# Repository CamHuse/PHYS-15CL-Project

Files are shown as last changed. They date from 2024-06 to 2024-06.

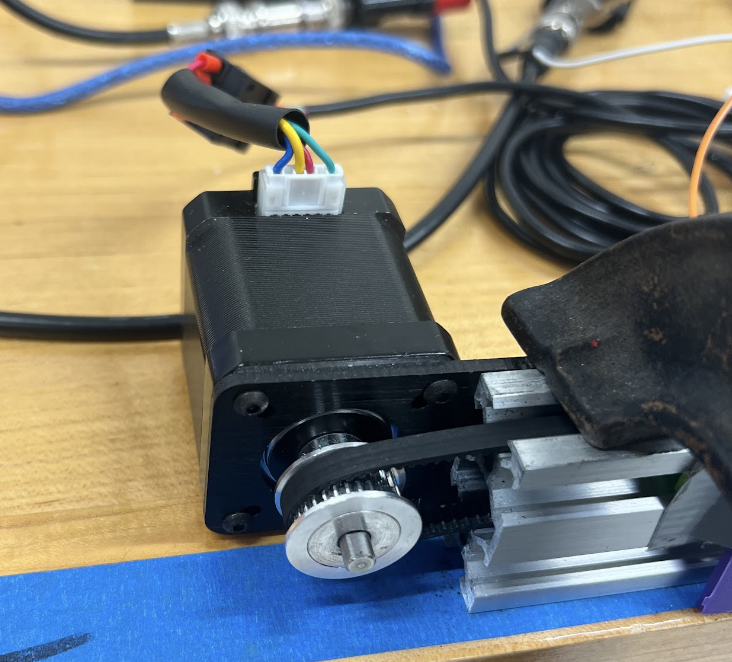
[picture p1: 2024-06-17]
.assets/StepperMotor.png

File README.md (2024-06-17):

# Inverted Pendulum

This GitHub repository documents the project completed by Eliott Schaffer, Jeremy Lauro, and Cameron Huse for PHYS 15C at UCSB during the Spring Quarter of 2024.

Each folder contains different aspects of the project, including significant files and specific documentation.

[Link to Presentation with Photos and Video Demonstrations](https://docs.google.com/presentation/d/1EEgrXbiuC8zDKRkNd1JOHVO5JtM1_9yI2Myhj0fMQJY/edit?usp=sharing)

## Schematic

A full quality version is also [avaliabe](https://github.com/CamHuse/PHYS-15CL-Project/blob/d5d5c650847254214024270f439a0aa117e3549a/Control%20Code/IntervedPendulum_SCH.pdf)

## Assembly Instructions:

1. Order the necessary parts.
2. Print the final version of the 3D models.
3. Construct the base rail system.
4. Attach the 3D printed parts to the moving cart and install the endstop switches.
5. Attach the encoder, ball bearings, and pendulum rod to the cart.
6. Wire the encoder and endstop switches to the Arduino as described in the schematic.
7. Wire the stepper motor controller to the Arduino as described in the schematic.
8. Wire the 24V DC supply to the stepper motor controller and connect the 4 stepper wires.
9. Run the Arduino Mega.

## Components

Inverted Pendulum System

### Cart

The cart consists of a base plate that holds the wheels connected to the rail and two 3D-printed pieces that serve as the base for the pendulum. It moves along a rail and supports the encoder and pendulum. The cart's design ensures precise movement and stability during operation.

### Pendulum

The pendulum is mounted on the cart and connected to the rotary shaft via a T-bracket. It swings freely, and its horizontal shaft is connected to the encoder, allowing us to read the pendulum's position at any moment in time.

### Encoder

The encoder, situated on the cart, measures the pendulum's angular position and velocity. It communicates with the Arduino via SPI (Serial Peripheral Interface), providing real-time positional data for system control and analysis.

System Close-Up

### Limit Switches

Limit switches are installed to detect the center of the rail and prevent the cart from exceeding the rail boundaries. These switches are electrically connected to the Arduino via interpret pins, allowing us to immediately stop the motor if the cart drifts too far either way.

Assembled System

### Stepper Motor

The stepper motor drives the cart along the rail. We control the motor by continuously sending a PWM signal to specify its desired speed. It is connected to the cart through a pulley system and powered by a 24V DC supply, with control signals provided by the Arduino.



---

## Swing-Up Phase
The swing-up logic aims to align the pendulum upright relative to its zero point, directly downward. When the pendulum is to the right of the zero point (positive angle), the system directs the cart right, applying torque to increase the pendulum's kinetic energy. Conversely, when the pendulum is to the left of the zero point (negative angle), the system directs the cart left. This repeated motion helps the pendulum swing back and forth, gradually reaching a vertical position while keeping the cart within the rail's limits. Below is a plot of the pendulum's angle overtime during the swing-up phase.



--
## Control System



### Sensors

The sensors used in this control system are responsible for gathering input data from the environment. They provide crucial information that the controller utilizes to make decisions and adjustments. The sensors included are:

- Absolute Encoder
- End-Stop Switches
- Computer Interface

### Controller

The controller processes the data received from the sensors and determines the appropriate actions to achieve the desired system behavior or state. This project utilized a PID controller. For a detailed explanation, see the control code folder in our repository.

### Actuators

Actuators are devices the system's controller controls to guide the system into the desired state. The only actuator utilized in this system is the stepper motor.

## Notes For Future Builders

Instead of getting a Nema17 Stepper motor kit, opt for a Nema23 kit. We were having over-torquing problems. 

Steel rotary shafts are hard to use and get a ball bearing on, and it is much easier to add threads to an aluminum rod and file it. 

Going with a DC motor design is more conventional and will allow for more direct torque control compared to a stepper motor.

If going for a stepper motor design, MATLAB and Raspberry Pis are too slow to count the steps of the stepper motor, a different design philosophy or extra distance sensor must be used.

--

Feel free to explore the repository and refer to the provided documentation for more details on each part of the project.

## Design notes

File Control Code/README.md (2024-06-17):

## Files

- `PIDPendulumControl.ino`: Implementation of PID control for the inverted pendulum.
- `README.md`: Documentation file.
  
## PID Control

Proportional-Integral-Derivative (PID) control is a feedback mechanism widely used in control systems. It calculates an error value as the difference between a desired setpoint and a measured variable. In our case, the measured variable is the angle of the pendulum provided by the absolute encoder, and the desired setpoint is 180 degrees from vertically down. The controller attempts to minimize the error by adjusting the process using three terms: proportional $(K_p)$, integral $(K_i)$, and derivative $(K_d)$.

### PID Control Implementation 

The control output $u(t)$, used to control the speed of the stepper motor, is given by:

$$ u(t) = K_p e(t) + K_i \int e(t)  dt + K_d \frac{d e(t)}{d t} $$

Where:
- $e(t)$ is the error at time $t$.
- $K_p$ is the proportional gain.
- $K_i$ is the integral gain.
- $K_d$ is the derivative gain.
  
Note: The parameters $\( K_p \)$, $\( K_i \)$, and $\( K_d \)$ defined in `PIDPendulumControl.ino` are specific to our cart-pendulum system with a pendulum mass and weight particular to our system, so they may not be directly applicable to other systems without retuning. Adjust these parameters based on your specific system's dynamics to achieve optimal control performance.

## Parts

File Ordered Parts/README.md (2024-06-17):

# Inverted Pendulum Ordered Parts

This repository contains 3D models for components used in our inverted pendulum project.

### Components:

- **Threaded Rotary Shaft:** Primary rotary shaft integrated into the Hub, featuring threads for connection to the T-Bracket.

- **CUI_Device:** Encoder used to measure the angle of the inverted pendulum.

- **Hub Pad:** Main cart connecting to the rail and pulley system, with the hub attaching for movement.

- **MS085 (Limit Switch):** Used to detect the ends of the rail and prevent the cart from running off.

- **V-Slot Belt Driven Actuator:** Model of the rail system without attached inverted pendulum components.

### Parts List
For an exhaustive list of the parts used in this project, please refer to the [Parts List](https://docs.google.com/spreadsheets/d/1zZ4MJvw8T9NZ0qEtBUQf3BjHz44bl6Pn-mwk28OsQ0s/edit?usp=sharing).

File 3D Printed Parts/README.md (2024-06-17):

This folder contains all the 3D models for parts used to assemble the inverted pendulum. The parts are as follows:

- **Ball Bearing Holder**: Secures the ball bearing in place on the Hub.
- **Bracket Rail Connector**: Attaches the Switch Bracket to the rail.
- **Hub**: Houses the encoder, rotary shaft, and ball bearings needed for the inverted pendulum. The Hub connects to the cart, allowing the entire inverted pendulum system to move.
- **Spacer**: A spacer was needed to correctly assemble the pulley system, as the one that was ordered was too small.
- **Switch Bracket**: Houses the limit switches and connects them to the rail.
- **T-Bracket**: Connects the rotary shaft to the main inverted pendulum rod.

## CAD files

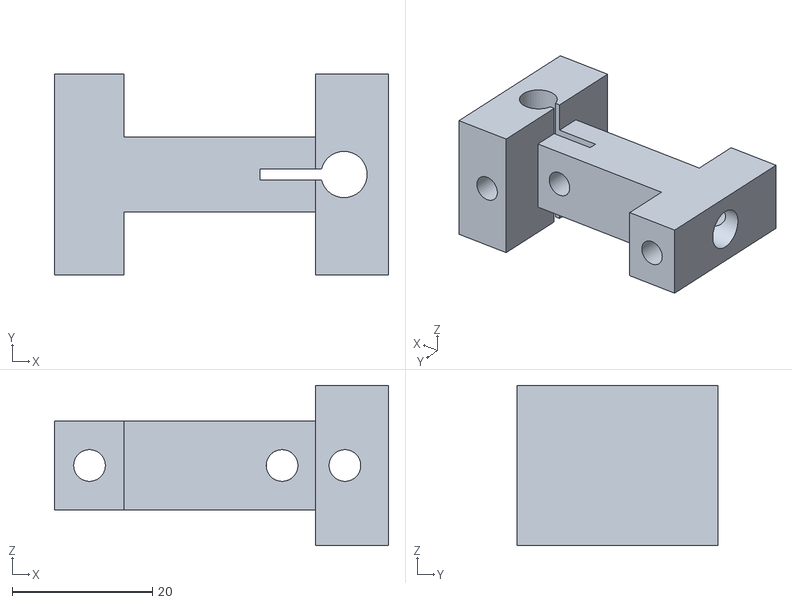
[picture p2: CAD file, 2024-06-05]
3D Printed Parts/T-Bracket Version 2 v19.stl
47.7 x 28.7 x 22.9

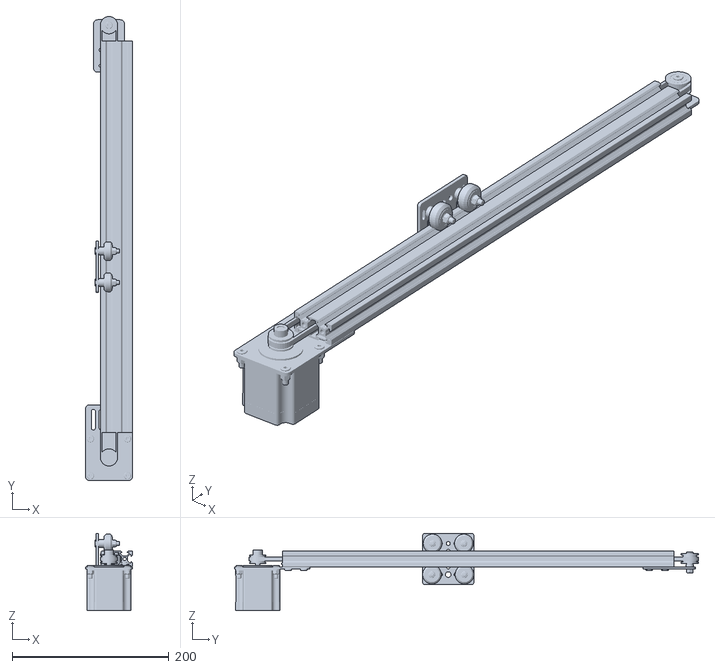
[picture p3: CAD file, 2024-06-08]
Ordered Parts/Nema 23 V-Slot Belt Driven Actuator v3.stl
60.0 x 592.6 x 98.6

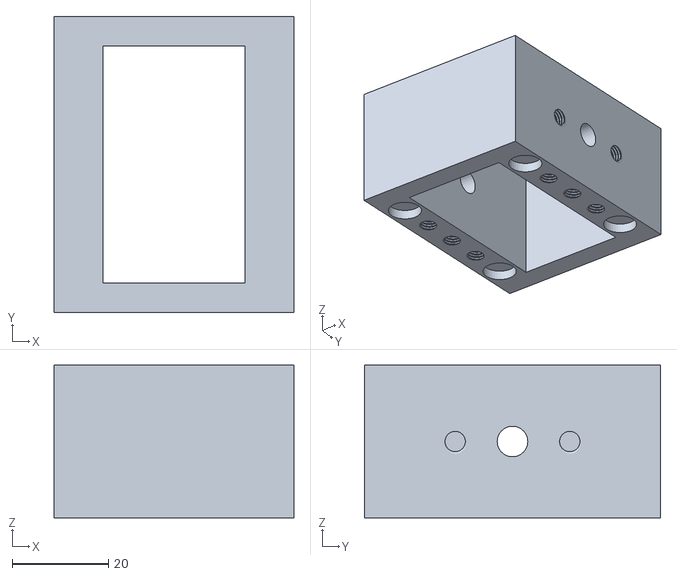
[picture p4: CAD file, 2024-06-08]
Prototype 3D Prints/Hub Design v7.stl
49.9 x 61.5 x 31.8

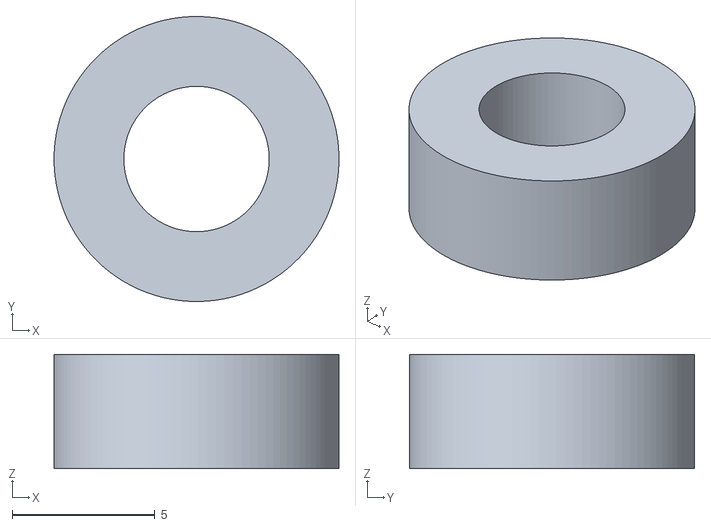
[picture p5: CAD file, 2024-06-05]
3D Printed Parts/Spacer v2.stl
10.00 x 10.00 x 4.00

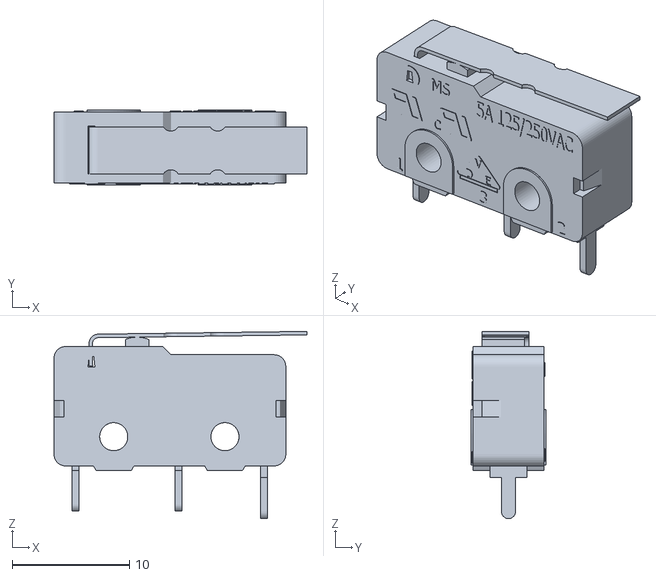
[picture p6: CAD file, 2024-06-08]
Ordered Parts/MS085xx02FxxxP1A v2.stl
21.6 x 6.40 x 16.0

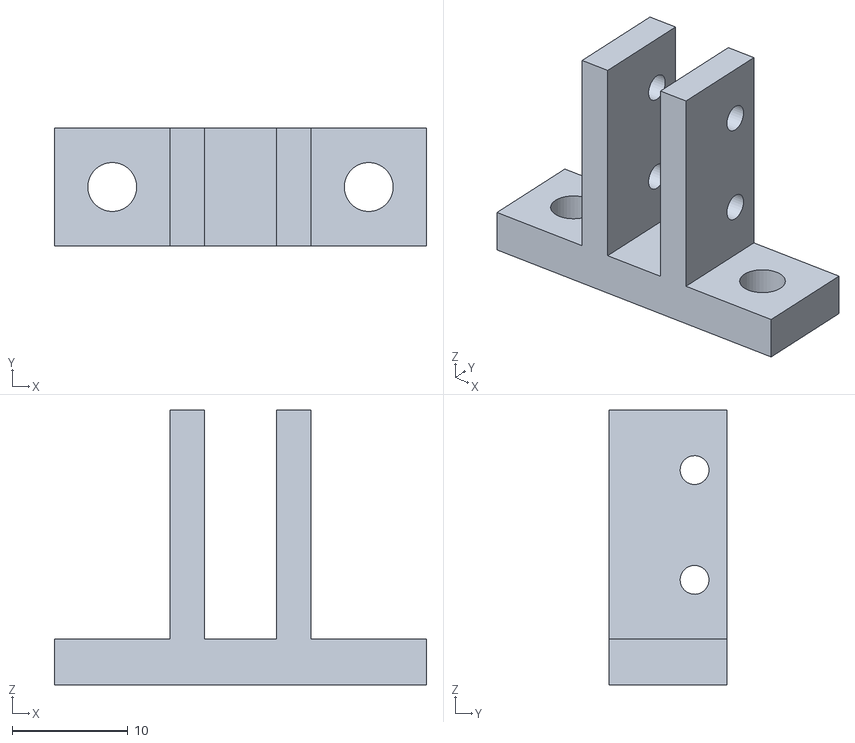
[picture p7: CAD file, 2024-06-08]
Prototype 3D Prints/Switch Bracket v3.stl
32.2 x 10.2 x 23.8

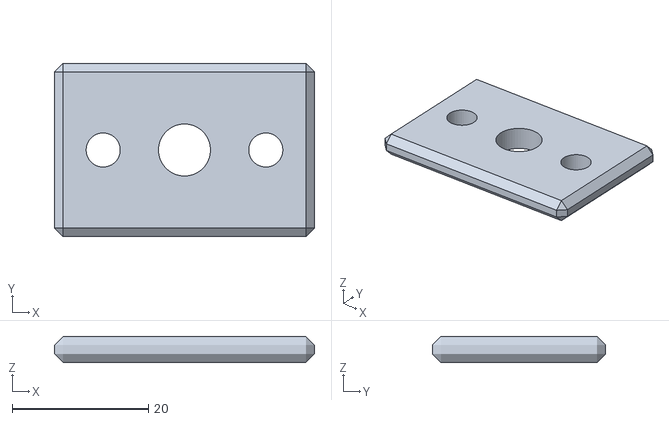
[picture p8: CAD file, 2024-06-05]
3D Printed Parts/Ball Bearing Holder v3.stl
38.1 x 25.4 x 3.81

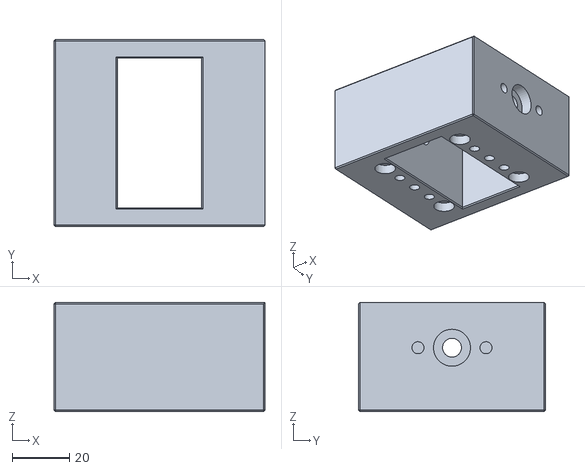
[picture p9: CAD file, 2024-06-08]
Prototype 3D Prints/Hub Design Version 2 v9.stl
73.9 x 65.5 x 38.2

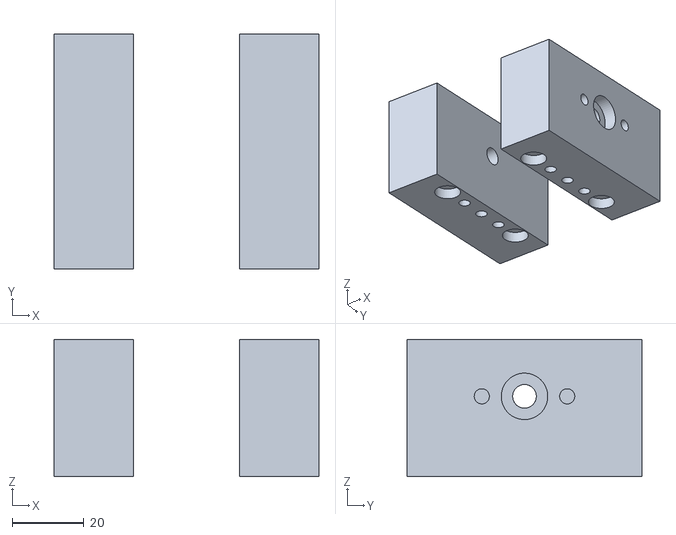
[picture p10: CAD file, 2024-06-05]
3D Printed Parts/Hub Design Version 3 v4.stl
73.9 x 65.5 x 38.2

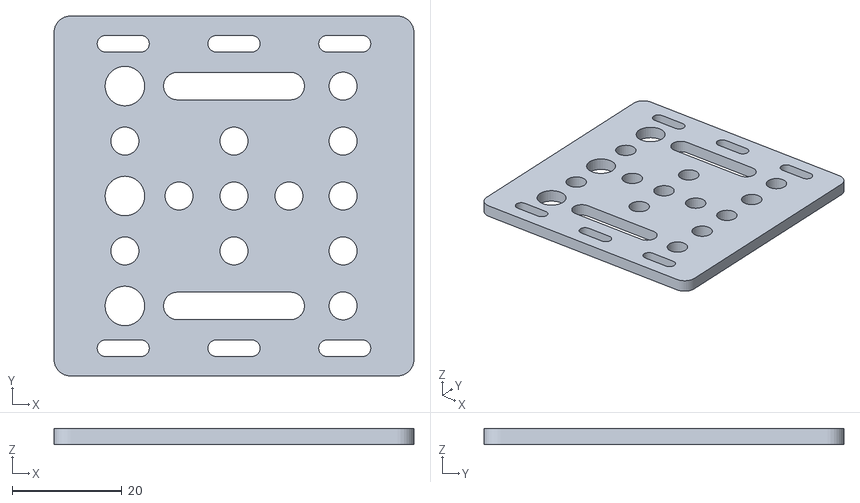
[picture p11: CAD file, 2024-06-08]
Ordered Parts/Hub Pad v1.stl
65.5 x 65.5 x 3.00

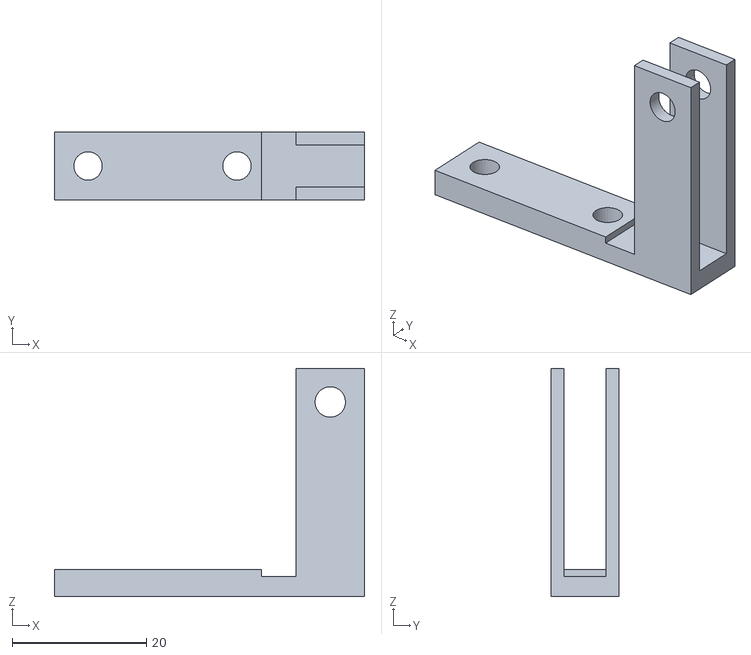
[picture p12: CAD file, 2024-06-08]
Prototype 3D Prints/Switch Bracket Version 2 v5.stl
46.2 x 10.2 x 34.0

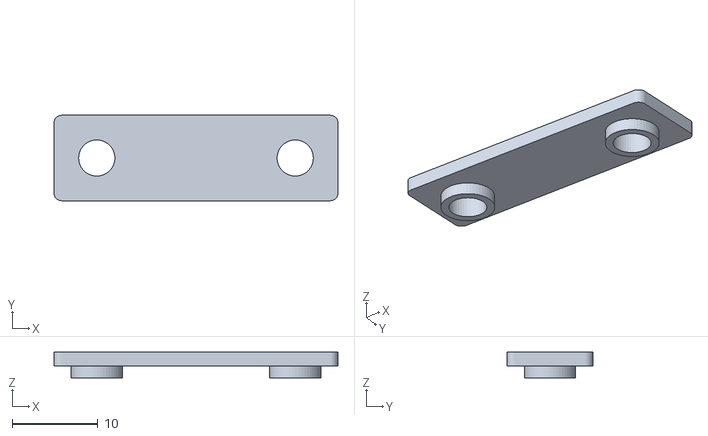
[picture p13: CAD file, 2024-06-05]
3D Printed Parts/Bracket Rail Connector v5.stl
33.2 x 10.0 x 3.00

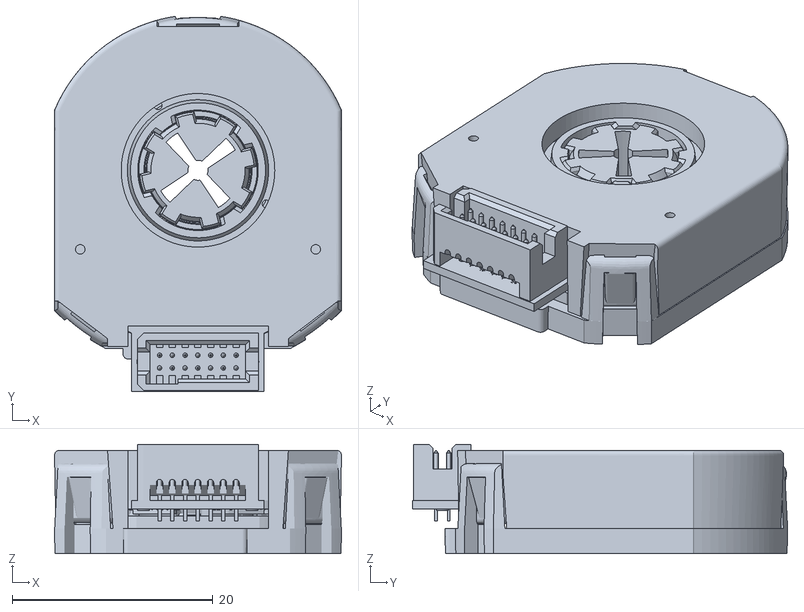
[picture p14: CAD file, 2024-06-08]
Ordered Parts/CUI_DEVICES_AMT203-0096-2000-S v2.stl
28.6 x 37.4 x 10.9

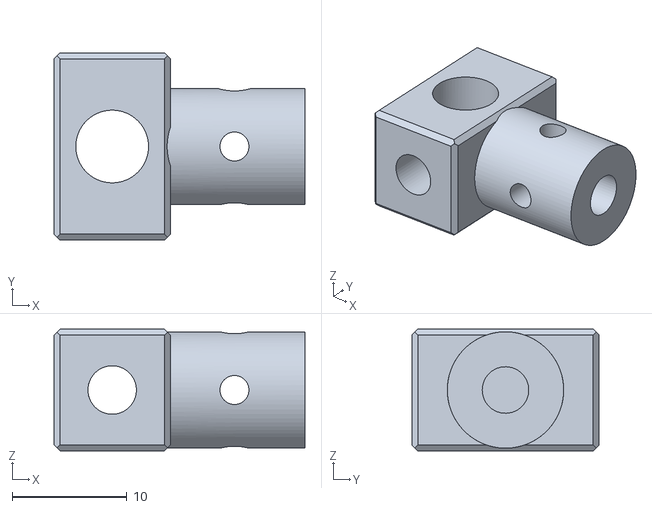
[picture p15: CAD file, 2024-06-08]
Prototype 3D Prints/T-Bracket Design v2.stl
21.9 x 16.3 x 10.6

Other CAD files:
3D Printed Parts/Switch Bracket Version 3 v5.stl
Ordered Parts/4166N16_Threaded Rotary Shaft v2.stl

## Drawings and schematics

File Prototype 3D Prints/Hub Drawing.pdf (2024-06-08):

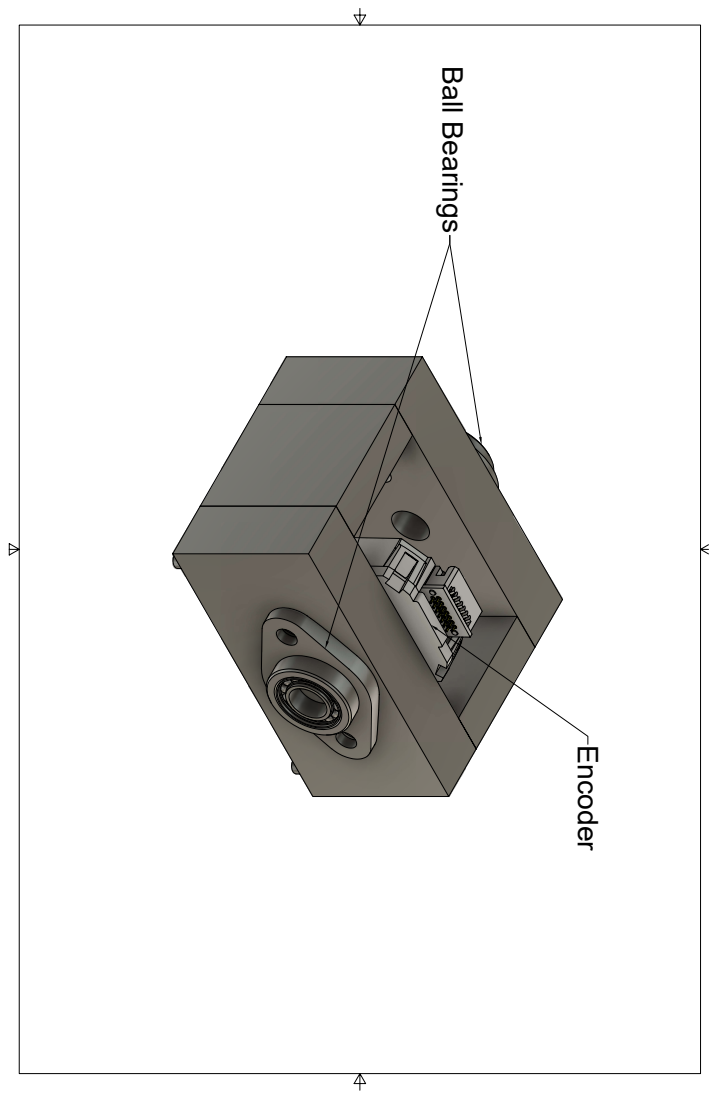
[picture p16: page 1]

Ball Bearings Encoder

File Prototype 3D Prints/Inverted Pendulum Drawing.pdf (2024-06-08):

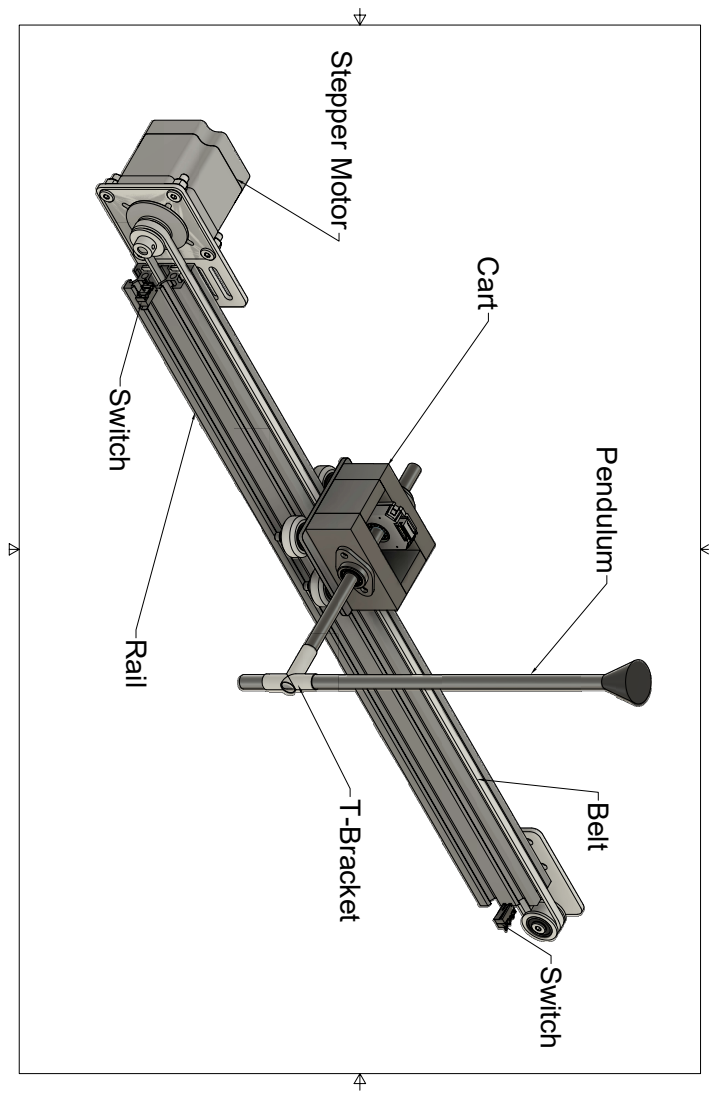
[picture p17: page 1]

Cart Stepper Motor Rail T-Bracket Belt Pendulum Switch Switch

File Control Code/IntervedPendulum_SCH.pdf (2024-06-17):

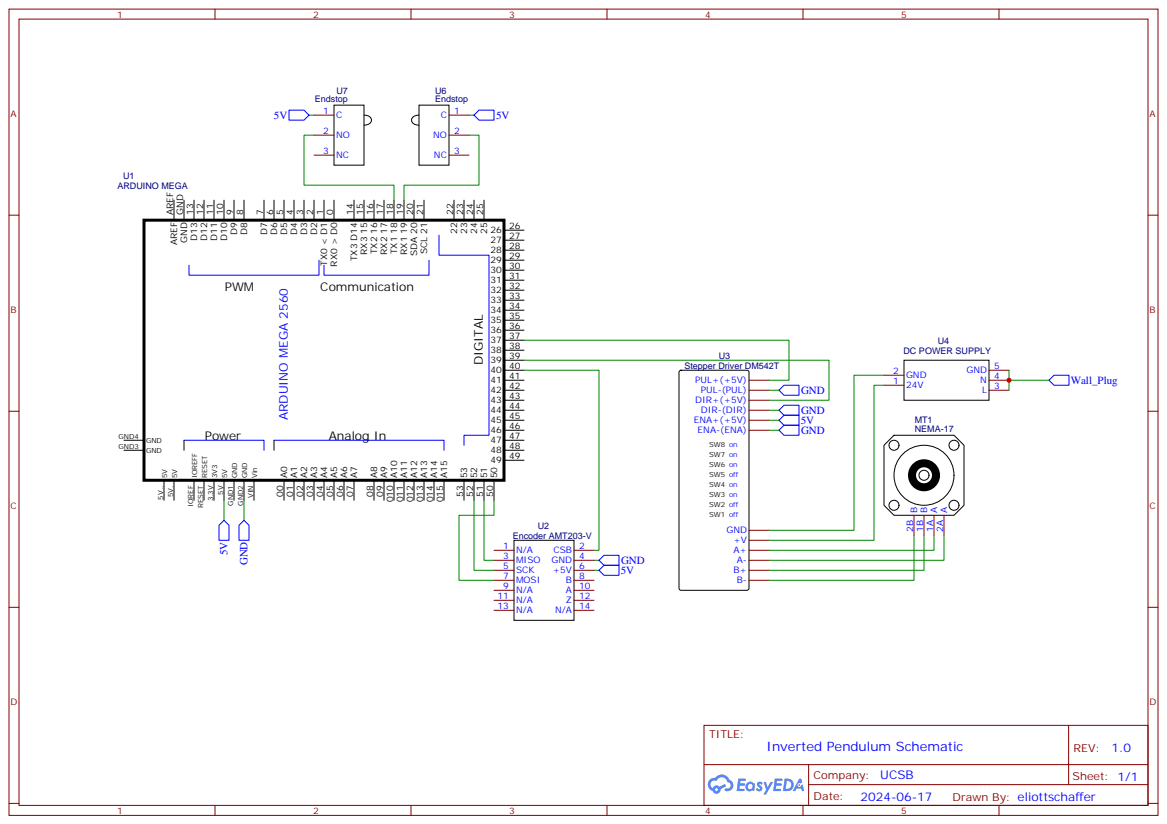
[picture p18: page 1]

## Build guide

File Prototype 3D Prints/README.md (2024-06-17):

# Inverted Pendulum 3D Models

This repository contains 3D models representing prototype designs and rough technical sketches for the final 3D-printed parts used in the inverted pendulum project.

## Prototype 3D Models

- Hub Design
- Hub Design Version 2
- Switch Bracket
- Switch Bracket Version 2
- T-Bracket Design

## Rough Sketches

- Hub
- Hub Drawing
- Inverted Pendulum
- Inverted Pendulum Drawing

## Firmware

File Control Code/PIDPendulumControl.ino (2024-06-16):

#include <AccelStepper.h>
#include <PID_v1.h>
#include <SPI.h>
#include <TimerThree.h>
#include <RTClib.h>

// Pin Definitions
#define CS 40 // Chip or Slave select
#define STEP_PIN 37
#define DIR_PIN 39
#define LS 18
#define RS 19
#define ENA 34

// Real-time clock instance
RTC_DS3231 rtc;

// Flags and control variables
volatile bool rightStopTriggered = false;
volatile bool leftStopTriggered = false;
volatile bool stabilize = false;

double last_output = 0.0;
long leftStopPosition = 0;
long rightStopPosition = 0;

// Encoder variables
uint16_t ABSposition = 0;
uint16_t ABSposition_last = 0;
uint8_t temp[2]; 

// PID control variables
double setpoint = 0.0;
volatile double input = 0.0;
double output = 0.0;
double outputLimit = 100;

// PID tuning parameters
float Kp = 1000.0;
float Ki = 0.0;
float Kd = 1.5;

// AccelStepper instance
double maxSpeed = 20000;
double acceleration = 7000;
AccelStepper stepper(AccelStepper::DRIVER, STEP_PIN, DIR_PIN);

// PID instance
PID myPID(&input, &output, &setpoint, Kp, Ki, Kd, DIRECT);
double ratio = maxSpeed / outputLimit;

// Setup function
void setup() {
    // Initialize pins and SPI
    pinMode(CS, OUTPUT); 
    digitalWrite(CS, HIGH);
    SPI.begin();
    SPI.beginTransaction(SPISettings(20000000, MSBFIRST, SPI_MODE0));
    SPI.setClockDivider(SPI_CLOCK_DIV32);
    
    // Initialize serial communication
    Serial.begin(115200);
    Serial.println("starting");
    Serial.flush();
    delay(2000);

    // Initialize control pins and interrupts
    pinMode(ENA, OUTPUT);
    pinMode(LS, OUTPUT);
    pinMode(RS, OUTPUT);
    attachInterrupt(digitalPinToInterrupt(LS), leftStopISR, CHANGE);
    attachInterrupt(digitalPinToInterrupt(RS), rightStopISR, CHANGE);

    // Initialize stepper motor
    digitalWrite(ENA, LOW);
    stepper.setMaxSpeed(maxSpeed); 
    stepper.setAcceleration(acceleration);

    // Initialize PID controller
    myPID.SetMode(AUTOMATIC);
    myPID.SetOutputLimits(-outputLimit, outputLimit); 

    // Initialize Timer3 for stepper speed control
    Timer3.initialize(2000000 / stepper.speed());
    Timer3.attachInterrupt(stepperInterrupt);
}

// Main loop
void loop() {

    while (true) {
        // Handle end stops
        if (rightStopTriggered) {
            rightStop();
            rightStopTriggered = false;
        }
        if (leftStopTriggered) {
            leftStop();
            leftStopTriggered = false;
        }

        // Read encoder and control movement
        readEncoder();
        Serial.println(input); 
        
        // Swing-up logic
        if (input > 0) {
            stepper.setSpeed(1100); // Move right
        } else {
            stepper.setSpeed(-1100); // Move left
        }

        if (abs(input) < 1.0) {
            break;
        }
    }
    stabilize = true;

    // Stabilization loop
    while (stabilize) {
        // Handle end stops
        if (rightStopTriggered) {
            rightStop();
            rightStopTriggered = false;
        }
        if (leftStopTriggered) {
            leftStop();
            leftStopTriggered = false;
        }

        // Read encoder and update PID
        readEncoder();
        last_output = output;
        myPID.Compute();
        updateSpeed(output * ratio);
        Serial.println(stepper.speed());
    }
}

// PID and speed control functions
void updateSpeed(double targetSpeed) {
    static double previousSpeed = last_output;
    double speedDifference = targetSpeed - previousSpeed;

    if (abs(speedDifference) < acceleration) {
        previousSpeed = targetSpeed;
    } else if (speedDifference > 0) {
        previousSpeed += acceleration;
    } else {
        previousSpeed -= acceleration;
    }

    stepper.setSpeed(previousSpeed);
}

// Initial swing function
void initialSwing() {
    unsigned long startTime = millis();
    const unsigned long swingDuration = 300; 

    // Move the cart right briefly
    while (millis() - startTime < swingDuration) {
        stepper.runSpeed();
    }

    // Move the cart left briefly
    startTime = millis();
    while (millis() - startTime < swingDuration / 2) {
        stepper.setSpeed(-1000);
    }
    while (millis() - startTime < swingDuration) {
        stepper.setSpeed(1000);
    }
}

// Timer interrupt for stepper control
void stepperInterrupt() {
    stepper.runSpeed(); 
}

// SPI transaction function
uint8_t SPI_T(uint8_t msg) {
    uint8_t msg_temp = 0; 
    digitalWrite(CS, LOW); 
    msg_temp = SPI.transfer(msg); 
    digitalWrite(CS, HIGH); 
    return (msg_temp); 
}

// Encoder reading function
void readEncoder() {
    uint8_t received = 0xA5; 
    ABSposition = 0; 

    digitalWrite(CS, LOW);
    SPI_T(0x10); 
    received = SPI_T(0x00); 

    while (received != 0x10) {
        received = SPI_T(0x00); 
        delay(2);
    }

    temp[0] = SPI_T(0x00); 
    temp[1] = SPI_T(0x00); 
    digitalWrite(CS, HIGH);
    temp[0] &= ~0xF0; 

    ABSposition = temp[0] << 8; 
    ABSposition += temp[1]; 

    if (ABSposition != ABSposition_last) {
        ABSposition_last = ABSposition; 
        input = round((ABSposition * 0.17579) - 360); 
    }
    if (abs(input) < 5.0) {
        input = 0.0;
    }
}

// Function to set zero point
void setZeroPoint() {
    digitalWrite(CS, LOW); 
    SPI.transfer(0x70); 
    digitalWrite(CS, HIGH); 
}

// Stop switch ISR functions
void leftStopISR() {
    leftStopTriggered = true;
}

void rightStopISR() {
    rightStopTriggered = true;
}

// Stop switch handling functions
void leftStop() {
    stepper.setSpeed(-1000);  
    unsigned long startTime = millis();
    const unsigned long reverseDuration = 300;  

    while (millis() - startTime < reverseDuration) {
        stepper.runSpeed();
    }

    digitalWrite(ENA, HIGH); 
}

void rightStop() {
    stepper.setSpeed(1000);  
    unsigned long startTime = millis();
    const unsigned long reverseDuration = 300;  

    while (millis() - startTime < reverseDuration) {
        stepper.runSpeed();
    }

    digitalWrite(ENA, HIGH); 
}

// Function to find center position
void findCenterPosition() {
    // Move to the left until the left switch is triggered
    stepper.setSpeed(400); 
    while (!leftStopTriggered) {
        stepper.runSpeed();
    }
    leftStopPosition = stepper.currentPosition();
    Serial.print(leftStopPosition);
    leftStopTriggered = false;

    // Move to the right until the right switch is triggered
    stepper.setSpeed(-400); 
    while (!rightStopTriggered) {
        stepper.runSpeed();
    }
    rightStopPosition = stepper.currentPosition();
    Serial.print(rightStopTriggered);
    rightStopTriggered = false;

    // Calculate the center position
    long centerPosition = (leftStopPosition + rightStopPosition) / 2;
    Serial.print(centerPosition);

    // Move to the center position quickly
    stepper.moveTo(centerPosition);
    stepper.setSpeed(400);
    while (stepper.distanceToGo() != 0) {
        stepper.runSpeedToPosition();
    }
}

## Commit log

2024-06-05 Added the STL for the final parts
    [Ball Bearing Holder v3.stl, Bracket Rail Connector v5.stl, Hub Design Version 3 v4.stl, Spacer v2.stl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]
2024-06-11 Rename README.md to 3D Printed Parts.md
2024-06-11 Rename 3D Printed Parts.md to README.md
